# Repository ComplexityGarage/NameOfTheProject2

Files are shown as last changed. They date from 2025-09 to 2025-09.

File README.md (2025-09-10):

# FLEXI-FRAME (Flexible Irradiation Frame System)
<p align="center">
    Description
</p>

# Authors 
- Karolina Klimek
- Pablo Vidal Franco

# Description of the project 
FLEXI-FRAME (Flexible Irradiation Frame System) is a modular system of movable frames, which can be used to irradiate samples (e.g. shielding materials), with a particle beam, such as a proton beam. Thanks to its modular structure you can piece together as many frames as you want! It is possible to place a material under tests on the frames and then remotely put the next layers of the material in the trajectory of the beam, in a subsequent manner. It allows you to check how the transmission changes without accessing the irradiation room many times, which helps to save expensive beam time and reduce unnecessary exposure of personnel to residual radiation. 

# Science and tech used 

## List of materials
Parts needed to make one FLEXI-FRAME: <br />
- RaspberryPi 5 <br />
- Micro Servo 9g SG90 (https://botland.com.pl/serwa-typu-micro/13128-serwo-sg-90-micro-180-5904422350338.html) <br />
- Breadboard <br />
- 220 $\mu F$ capacitor <br />
- 470 $\Omega$ resistor <br />
- LED (2.5-3.7 V)
- Two M2 x 10mm screws <br />
- Screw terminal
- USB-C power adapter (5 V 3 A)
- Servo horn

## Servo specifications
- Logic level compatibility 3.3 V logic
- Operating voltage 4.8 V - 6.0 V
- Average running current: 250 mA
- Stall current: 360 mA

## Power source for the servos
A standard phone charger USB-C power adapter (Dux Ducis) with an output of 5 V 3 A can be repurposed by cutting open the cable and separating VBUS and GND lines into a screw terminal, connected to a prototype breadboard rail power and GND rails.

The total available power is:

$$
P_{total} = 5\ \text{V} \cdot 3\ \text{A} = 15\ \text{W}
$$

Power consumption per servo is:

$$
P_{servo} = 5\ \text{V} \cdot 0.25\ \text{A} = 1.25\ \text{W}
$$

Maximum theoretical number of servos that this setup can handle:

$$
n_{servos} = \frac{P_{total}}{P_{servo}} = \frac{15\ \text{W}}{1.25\ \text{W}} = 12
$$

Therefore, assuming current draw remains consistent and below the 3 A limit, the USB-C adapter can power 4 servos stably.

## Capacitor for stability
To buffer transient load steps on the 5 V servo rail before the power supply fully responds, a 220 µF electrolytic low-ESR capacitor is placed across +5 V and GND near the servo power split. Assuming $\Delta I$ is the current stall of a single servo (an upper bound of 360 mA), and assuming that only one servo will be operated at a given timestep, we have the following values:

$$
\Delta I = 0.36\ \mathrm{A},\quad
\Delta t = 2\ \mathrm{ms},\quad
C = 220\ \mu \text{F},\quad
V = 5\ \mathrm{V}
$$

The extra charge drawn by the step:

$$
\Delta Q = \Delta I\ \Delta t = 360\ \mathrm{mA} \cdot 2 \mathrm{ms} = 720 \ \mu \text{C}
$$

Now we can compare the capacitor stored charge ($Q_{total}$) against two scenarios:
- 1 servo demanding extra charge in a 2 ms step ($\Delta Q_{single} = 720 \ \mu \text{C}$)
- A worst-case scenario where 4 servos demand extra charge in a 2 ms step ($\Delta Q_{multiple} = 720 \ \mu \text{C} \cdot 4 = 2880\ \mu \text{C}$)

We compare the total charge stored by the 220 $\mu F$ capacitor against the two scenarios:

$$ Q_{total} = CV = 220\ \mu \text{F} \cdot 5\ \mathrm{V} = 1100\ \mu \text{C}, \quad \Delta Q_{single} \le Q_{total}, \quad \Delta Q_{multiple} \ge Q_{total}
$$

We can assume 10% of our 5 V budget to power the servos and compute how long can the USB-C power adapter fail in both scenarios:

$$
\Delta t_{\max}\ = \frac{C \cdot \Delta V_{\text{target}}\ }{\Delta I} = \frac{220\ \mu \text{F} \cdot 0.5\ \text{V}}{360\ \text{mA}} \approx 0.306 \mathrm{ms}
$$

$$
\Delta t_{\max}\ = \frac{C \cdot \Delta V_{\text{target}}\ }{\Delta I} = \frac{220\ \mu \text{F} \cdot 0.5\ \text{V}}{1440\ \text{mA}} \approx 0.076 \mathrm{ms}
$$

We can conclude that the current capacitor system could handle a single servo stalling during transient current supply ($\le0.306\ \text{ms}$) while limiting voltage droop to 0.5 V (10% of the 5 V needed for servo operation), but could not handle 4 servos stalling at the same time unless the USB-C power adapter recovers in less than 0.076 ms. 

## Wiring diagram
<p align="center">
pic_garage
</p>

## Assembly instructions
To build one FLEXI-FRAME couple of parts need to be 3D printed - .STL files for 3D printing are available in [STL_files](./STL_files/) directory. Constructing one frame requires 5 pieces: frame with a rack, pinion gear, rack holder-top, rack holder-bottom and puzzle servo-frame box. Instructions how to assemble the frame are available [here](./How_to_assemble_a_frame.md). <br />
The concept of using a servo mechanism to convert circular motion into linear motion was inspired by this video: https://www.youtube.com/watch?v=2vAoOYF3m8U. The design was subsequently adapted and modified, including changes to the mechanical layout and the use of a different servo. <br />

# State of the art 
FLEXI-FRAME, in its first prototype version, allows you to build a modular frame system and remotely control the frames in and out of the beam's trajectory. With the current design you can stack up to 4 frames, using servos sequentially.

# What next?
- Creating a rail structure to ensure stable linear motion when moving the frame in or out.
- Wiring frame-motion sensors and building a UI interface that lets the user know what is the current state of each frame.
- Improve the capacitor buffer system to support up to $n_{servos}$ in a worst-case scenario, to allow safer multiple non-sequential servo operation.

# Sources 
- Converting circular motion into linear motion using a servo mechanism (https://www.youtube.com/watch?v=2vAoOYF3m8U)
- Servo specs (https://protosupplies.com/product/servo-motor-micro-sg90/)

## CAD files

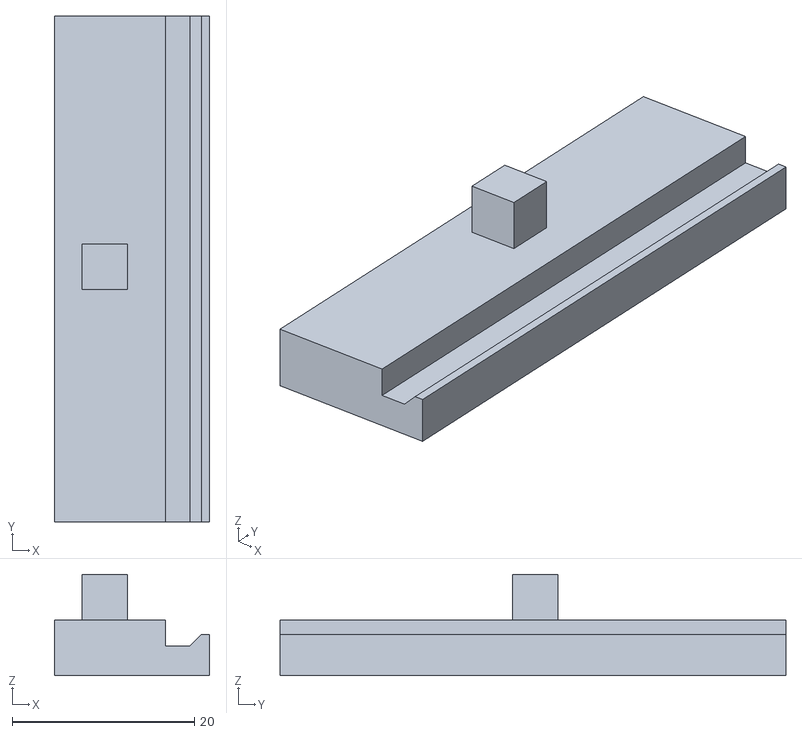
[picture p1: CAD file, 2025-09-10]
STL_files/rack holder-top.stl
17.0 x 55.5 x 11.1

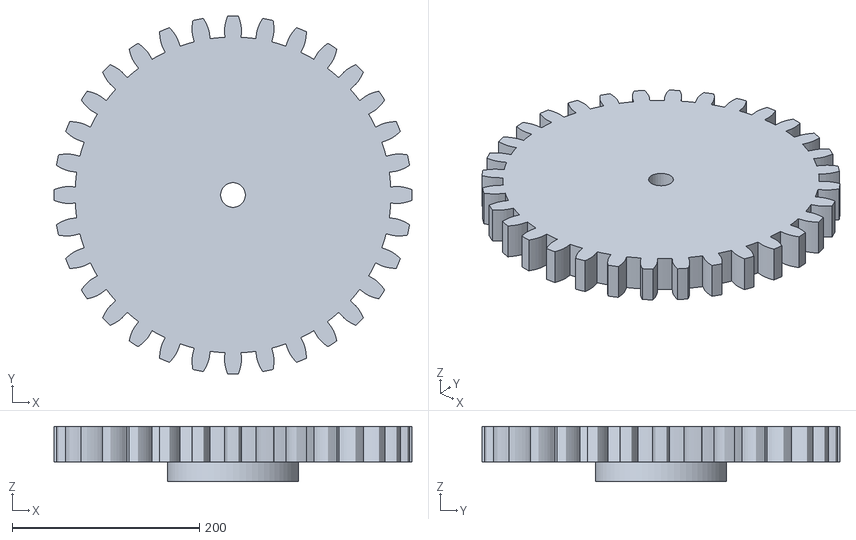
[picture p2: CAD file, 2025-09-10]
STL_files/pinion gear.stl
382.5 x 382.5 x 59.0

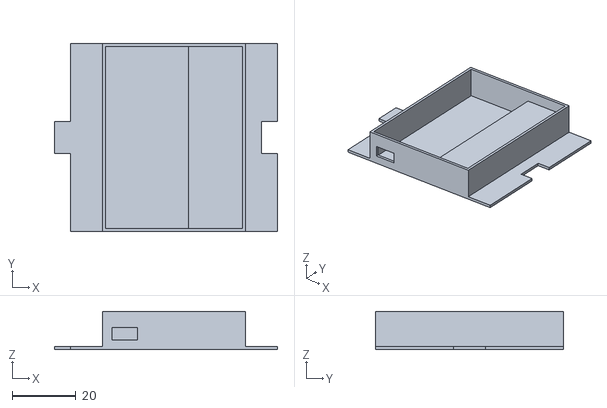
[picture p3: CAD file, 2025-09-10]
STL_files/puzzle servo-frame box.stl
70.0 x 59.0 x 12.0

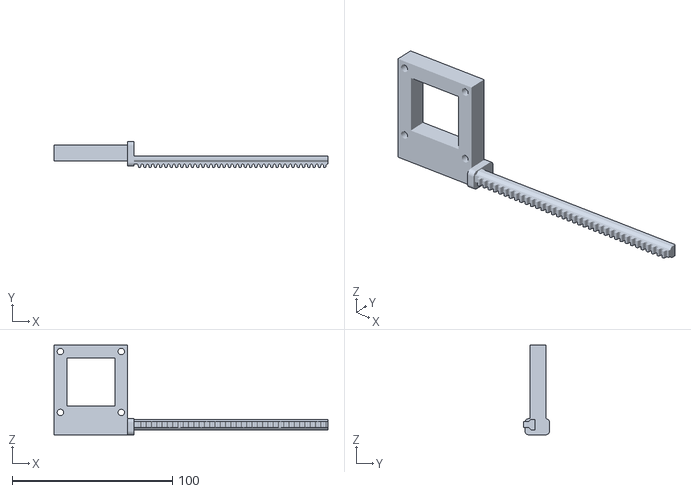
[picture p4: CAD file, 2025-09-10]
STL_files/frame with a rack.stl
171.0 x 16.3 x 56.0

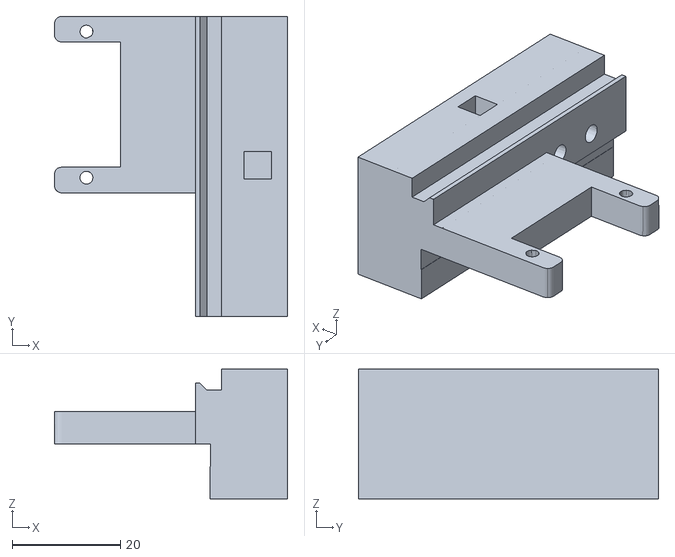
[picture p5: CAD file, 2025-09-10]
STL_files/rack holder-bottom.stl
43.0 x 55.5 x 24.0

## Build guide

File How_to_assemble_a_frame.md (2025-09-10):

# How to assemble a frame?
You need to connect rack holder-top and rack holder-bottom together. Then using the M2 x 10 mm screws attach servo to the rack holder. <br /> <br />
The pinion gear needs also some modifications. To make a working pinion gear you need to take one of the horns, which are usually available together with the servo, and cut the arm, such that only the round part remains. It is probably the best to take the horn with only one arm, shown on the left photo below. After that this round part needs to be placed in the hole in the pinion gear - as presented on the right photo below.<br />
<p align="left">
    First
    Second
</p>  <br />
As a next step you need to insert the frame with a rack into the rail in the rack holder. The pinion gear can then be mounted onto the servo and the whole structure can be placed in the puzzle servo-frame box. <br />
